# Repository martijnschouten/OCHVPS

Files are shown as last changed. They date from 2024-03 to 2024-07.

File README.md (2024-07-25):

# OCHVPS: Octo-Channel High Voltage Power Supply

This git contains all the files to produce your own octo channel high voltage power supply. This is a 2 kV, 8 channel, 10 W power supply. It has 8 half-bridge outputs, each switching at up to 1 kHz. It can be used as 4 full bridges. Current monitoring on each channel. Designed to drive capacitive loads

HVPS

A block diagram of the power suply can be found below
HVPS_block

The source code of the Python GUI can be found in this [github repository](https://github.com/martijnschouten/OCHVPS_SW)

The source code of firmware running on microcontroller inside the board can be found in this [github repository](https://github.com/martijnschouten/OCHVPS_FW)

Some more information can be found in the [user's manual](https://github.com/martijnschouten/OCHVPS/blob/v1.0/1_DOC/OCHVPS_V1.0_User_Manual.pdf).

If your just interested in the schematic, that can be found [here](https://github.com/martijnschouten/OCHVPS/blob/v1.0/2_HW/PDF/ochvps_v1.0.pdf) 

OCHVPS © 2021-2024 by MBE <ochvps@proton.me>

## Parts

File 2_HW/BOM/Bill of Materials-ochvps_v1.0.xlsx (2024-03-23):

Designator | Quantity | Supplier 1 | Supplier Part Number 1 | Name | Description
C1, C3 | 2 | Farnell | 9227865 | C1206C105K3RACTU | Chip Capacitor, 1 uF, +/- 10%, 25 V, -55 to 125 degC, 1206 (3216 Metric), RoHS, Tape and Reel
C2, C4, C28 | 3 | Mouser | 80-C0603C104K3R | C0603C104K3RACTU | CAP CER 0.1UF 25V X7R 0603
C5, C6, C7, C8, C9, C10, C11, C12, C13, C14, C16, C17, C19, C20, C21, C22, C60_HB1, C60_HB2, C60_HB3, C60_HB4, C60_HB5, C60_HB6, C60_HB7, C60_HB8, C61_HB1, C61_HB2, C61_HB3, C61_HB4, C61_HB5, C61_HB6, C61_HB7, C61_HB8 | 32 | Mouser | 581-06033C104KAT4A | 06033C104KAT4A | CAP CER 0.1UF 25V X7R 0603
C15 | 1 | Digi-Key | 399-7411-1-ND | C0805C106K8RACTU | 0805 C 10uF Ceramic Multilayer Capacitor; 10 V; +125degC; X7R Dielectric; +/-10%
C18 | 1 | DigiKey | 445-5964-1-ND | C1608X5R1E225K080AB | Multilayer Ceramic Capacitors 2.2μF ±10% 25V X5R SMD 0603
C23, C24 | 2 | Digi-Key | 478-1167-1-ND | 06035A220JAT2A | Cap Ceramic 22pF 50V C0G 5% SMD 0603 125C Paper T/R
C25 | 1 | Digikey | P15460CT-ND | EEH-ZC1E560P | Cap Aluminum Polymer Hybrid 56uF 25VDC 20% (6.3 X 5.8mm) SMD 0.05 Ohm 900mA 4000h 125C Embossed T/R
C26 | 1 | Farnell | 3605828 | 16SVPG330MX | Capacitor, Polymer Aluminum, Radial, 7mOhm, 330 CAP, 16V, SVPG, Surface Mount
C27, C30, C55, C58, C62_HB1, C62_HB2, C62_HB3, C62_HB4, C62_HB5, C62_HB6, C62_HB7, C62_HB8, C63_HB1, C63_HB2, C63_HB3, C63_HB4, C63_HB5, C63_HB6, C63_HB7, C63_HB8 | 20 | Digikey | 445-1316-1-ND | C1608X7R1E104K080AA | TDK - C1608X7R1E104K080AA - Keramikvielschichtkondensator, SMD, 0.1 µF, 25 V, 0603 [Metrisch 1608], ± 10%, X7R, C Series
C29, C31 | 2 | Digikey | 399-C0805C226M8PAC7210CT-ND | C0805C226M8PAC7210 | Cap, 22UF, 10V, Mlcc, 0805;
C32, C48 | 2 | Digikey | 478-6637-1-ND | TCJD476M025R0060 | CAP TANT POLY 47UF 25V 2917
C33, C34, C35 | 3 | Digikey | 445-5720-1-ND | CGA6P1X7R1E106M250AC | Multilayer Ceramic Capacitors MLCC - SMD/SMT 1210 10uF 25volts X7R 20% T=2.5mm
C36, C37, C42 | 3 | Mouser | 581-06033D105MAT2A | 06033D105MAT2A | Cap Ceramic 1uF 25V X5R 20% SMD 0603 85C Paper T/R
C38, C49 | 2 | DigiKey | 445-7348-1-ND | C1005X7R1E104K050BB | TDK - C1005X7R1E104K050BB - SMD Multilayer Ceramic Capacitor, 0.1 µF, 25 V, 0402 [1005 Metric], ± 10%, X7R, C Series TDK
C39 | 1 | DigiKey | 445-6893-1-ND | CGA2B3X7R1H103K050BB | CAP CER 10000PF 50V X7R 0402
C40, C41 | 2 | DigiKey | 490-6049-1-ND | GCM188L81H104KA57D | MURATA - GCM188L81H104KA57D - CAP, MLCC, AEC-Q200, X8L, 0.1UF, 0603
C43, C44, C45, C46 | 4 | Mouser | 810-CGA5L1X7R1E106K | CGA5L1X7R1E106K160AC | CAP CERAMIC, 10UF, 25V, X7R, 1206; Product Range:TDK - CGA Series; Capacitance:10µF; Capacitance Tolerance:± 10%; Dielectric Characteristic:X7R; Voltage Rating:25V; Ceramic Capacitor Case:1206 ^3216 Metric]; Packaging:Cut Tape; MSL:-
C47 | 1 | Digikey | 399-16637-1-ND | T521D226M035ATE060 | Cap Tant Polymer 22uF 35V D CASE 20% (7.3 X 4.3 X 2.8mm) SMD 7343-31, D 60 mOhm 125°C T/R
C50 | 1 | Digi-Key | 445-5607-1-ND | CGA2B2X7R1H472K050BA | CAP CER 4700PF 50V X7R 0402
C51 | 1 | Digikey | 490-14349-1-ND | GCM1555C1H101FA16D | 0402 50V C0G 100pF 1% multilayer ceramic capacitor
C52 | 1 | DigiKey | 445-9118-1-ND | C1608X6S1C475K080AC | Cap Ceramic 4.7uF 16V X6S 10% SMD 0603 105C Paper T/R
C53 | 1 | Mouser | 581-08055C334KAT2A | 08055C334KAT2A | CAP CER 0.33UF 50V X7R 0805
C54, C59 | 2 | Digikey | 445-1287-1-ND | C1608C0G1H331J080AA | C Series 0603 330 pF 50 V ±5 % Tolerance C0G SMT Multilayer Ceramic Capacitor
C56, C57 | 2 | Mouser | 581-06035A100J | 06035A100JAT2A | AVX - 06035A100JAT2A - SMD Multilayer Ceramic Capacitor, 10 pF, 50 V, 0603 [1608 Metric], ± 5%, C0G / NP0, AVX 0603 MLCC
D1 | 1 | Digikey | F3157CT-ND | SP0504BAHTG | TVS DIODE 5.5V 8.5V SOT23-5
D2, D3, D4, D5 | 4 | Digikey | 641-1326-1-ND | CDBW0520L-G | DIODE SCHOTTKY 20V 500MA SOD123
D6 | 1 | Mouser | 863-SZMM3Z3V0T1G | SZMM3Z3V0T1G | Zener Diodes ZEN SOD323 REG 0.2W
FB1 | 1 | Digikey | 490-11045-1-ND | BLM21BD331SN1D | FERRITE BEAD 330 OHM 0805 1LN
H_GND | 1 | Digikey | 486-3654-ND | 0040.1101 | Test Jack; 2mm; 10A; PCB Mt; Single Cntct; 90-Degree; Thrmoplstc; Black; UL94V-2; PB 1101
H_HV1, H_HV2, H_HV3, H_HV4, H_HV5, H_HV6, H_HV7, H_HV8 | 8 | Digikey | 486-3655-ND | 0040.1102 | Test Jack; 2mm; 10A; PCB Mt; Single Cntct; 90-Degree; Thrmoplstc; Red; UL94V-2; PB 1101
J1 | 1 | Digikey | CP-063AH-ND | PJ-063AH | CONN PWR JACK 2X5.5MM SOLDER
J2 | 1 | Newark | 67T2260 | 10118194-0001LF | Micro USB B Type Receptacle, 1.8 A, -55 to 85 degC, 5-Pin SMD, RoHS, Tape and Reel
J3, J4 | 2 |  |  | CON10A
L1 | 1 | Mouser | 652-SRP1245A-4R7M | SRP1245A-4R7M | BOURNS SRP1245A-4R7M Surface Mount Power Inductor, SRP1245A Series, 4.7 H, 12 A, 27 A, Shielded, 0.015 ohm
LED1, LED3 | 2 | Digikey | 732-4983-1-ND | 150080GS75000 | SMD LED green 3.5 V 0805, 150080GS75000, Würth Elektronik
LED2 | 1 | Digikey | 350-2044-1-ND | 598-8170-107F | Single Color, 2 V, -30 to 85 degC, 2-Pin SMD (0805), RoHS, Tape and Reel
P1 | 1 | Digi-Key |  | FTSH-105-01-F-DV-K | Conn Unshrouded Header HDR 10 POS 1.27mm Solder ST SMD T/R
Q1 | 1 | Digikey | SSM3J358RLFCT-ND | SSM3J358R,LF | Small Low ON Resistance MOSFET P-Channel 20V 6A 3-Pin SOT-23F T/R
Q2, Q3 | 2 | Digikey | 296-49601-1-ND | CSD17579Q5A | MOSFET 30V N-Chan NexFET? Pwr MOSFET 8-VSONP
R1 | 1 | DigiKey | 311-47KGRCT-ND | RC0603JR-0747KL | Thick Film Resistor
R2, R3 | 2 | Farnell | 4013304 | RC0603FR-1333RL | RC Series 0603 33 Ohm ±1 % 0.1 W ±100 ppm/°C Surface Mount Thick Film Resistor
R4 | 1 |  |  | RES_0 | Thick Film Resistor
R5, R6, R7, R44, R45, R46, R47 | 7 | DigiKey | 311-0.0GRCT-ND | RC0603JR-070RL | RES SMD 0 OHM JUMPER 1/10W 0603
R8 | 1 | Digikey | 541-3993-1-ND | CRCW06034K70JNEA | RES Thick Film, 4.7kΩ, 5%, 0.1W, 200ppm/°C, 0603
R9, R10, R12, R13, R15, R16, R31, R41, R48_HB1, R48_HB2, R48_HB3, R48_HB4, R48_HB5, R48_HB6, R48_HB7, R48_HB8, R53_HB1, R53_HB2, R53_HB3, R53_HB4, R53_HB5, R53_HB6, R53_HB7, R53_HB8 | 24 | Digi-Key | 311-10.0KHRCT-ND | RC0603FR-0710KL | Res General Purpose Thick Film 0603 10K Ohm 1% 1/10W ±100ppm/°C Molded SMD Paper T/R
R11 | 1 | Mouser | 71-CRCW0603J-1.0M-E3 | CRCW06031M00JNEA | VISHAY - CRCW06031M00JNEA - SMD Chip Resistor, 0603 [1608 Metric], 1 Mohm, CRCW e3 Series, 75 V, Thick Film, 100 mW
R14, R17 | 2 | Digikey | 541-4022-1-ND | CRCW06032K20FKEA | SMD Resistor, Thick film 2.2 kOhm, ± 1 %, 0603, CRCW06032K20FKEA, Vishay
R18, R19 | 2 | Mouser | 71-CRCW060310K0FKEAC | CRCW060310K0FKEAC | Chip Resistor, 10 KOhm, +/- 1%, 100 mW, -55 to 155 degC, 0603 (1608 Metric), RoHS, Tape and Reel
R20, R40 | 2 | Digikey | 541-CRCW08054K70JNEBCT-ND | CRCW08054K70JNEB | VISHAY CRCW08054K70JNEB RES, THICK FILM, 4K7, 5%, 0.125W, 0805
R21 | 1 | Digikey | 541-CRCW08053K32FKEACCT-ND | CRCW08053K32FKEAC | Res Thick Film 0805 3.32K Ohm 1% 1/8W ±100ppm/°C Molded SMD Paper T/R
R22 | 1 | DigiKey | P1.07KHCT-ND | ERJ-3EKF1071V | Res Thick Film 0603 1.07K Ohm 1% 0.1W(1/10W) ±100ppm/C Pad SMD Automotive T/R
R23 | 1 | Digikey | 541-CRCW0805680RJNEBCT-ND | CRCW0805680RJNEB | Thick Film Resistors - SMD 1/8watt 680ohms 5%
R24 | 1 |  |  |  | Thick Film Resistor
R25 | 1 | Digikey | P37.4KDCCT-ND | ERA-2AEB3742X | RES SMD 37.4KOHM 0.1% 1/16W 0402
R26, R30 | 2 | Mouser | 603-RT0402BRE0710KL | RT0402BRE0710KL | RES SMD 10K OHM 0.1% 1/16W 0402
R27, R28 | 2 | Digi-Key | 311-1.00HRCT-ND | RC0603FR-071RL | Res General Purpose Thick Film 0603 1 Ohm 1% 1/10W ±200ppm/°C Molded SMD Paper T/R
R29 | 1 | DigiKey | P30.1KDCCT-ND | ERA-2AEB3012X | PANASONIC - ERA2AEB3012X - RES, 30K1, 0.1%, THIN FILM
R32 | 1 | Digikey | 541-49.9KAVCT-ND | CRCW040249K9DHEDP | RES SMD 49.9KOHM 0.5% 1/16W 0402
R33 | 1 | DigiKey | RMCF0402ZT0R00CT-ND | RMCF0402ZT0R00 | RES 0 OHM JUMPER 1/16W 0402
R34 | 1 | DigiKey | P0.01BVCT-ND | ERJ-8CWFR010V | RES 0.01 OHM 1% 1W 1206
R35, R36, R58_HB1, R58_HB2, R58_HB3, R58_HB4, R58_HB5, R58_HB6, R58_HB7, R58_HB8, R59_HB1, R59_HB2, R59_HB3, R59_HB4, R59_HB5, R59_HB6, R59_HB7, R59_HB8, Rsh1 | 19 | Digikey | RNCF0603AKT10R0CT-ND | RNCF0603AKT10R0 | RES 10 OHM 0.05% 1/10W 0603
R37 | 1 | Digikey | 541-CRCW0402150KFKTDCT-ND | CRCW0402150KFKTD | RES SMD 150K OHM 1% 1/16W 0402
R38 | 1 | Digikey | YAG3260CT-ND | RC0402FR-0793K1L | Res Thick Film 0402 93.1K Ohm 1% 0.063W(1/16W) ±100ppm/C Molded SMD Paper T/R
R39 | 1 | Mouser | 71-CRCW0402-10K | CRCW040210K0FKTD | Res Thick Film 0402 10K Ohm 1% 0.063W(1/16W) }100ppm/ ? SMD Automotive Paper T/R
R42 | 1 | Digikey | SM102031006FE-ND | SM102031006FE | Thick Film Resistors - Through Hole 100M ohms 1%
R43 | 1 | Mouser | 660-RN73R1JTD1503B25 | RN73R1JTTD1503B25 | Res 150K Ohm 0.1% 1/10W 0603
R49_HB1, R49_HB2, R49_HB3, R49_HB4, R49_HB5, R49_HB6, R49_HB7, R49_HB8, R54_HB1, R54_HB2, R54_HB3, R54_HB4, R54_HB5, R54_HB6, R54_HB7, R54_HB8 | 16 | Mouser | 667-ERJ-14YJ101U | ERJ-14YJ101U | SISTOR, THICK FILM, 1210, 100 OHM, 5%, 500mW; Product Range:PANASONIC - ERJ Series; Resistance:100ohm; Power Rating:500mW; Resistance Tolerance:± 5%; Resistor Case Style:1210 ^3225 Metric]; Resistor Element Type:Thick Film; MSL:-
R50_HB1, R50_HB2, R50_HB3, R50_HB4, R50_HB5, R50_HB6, R50_HB7, R50_HB8, R55_HB1, R55_HB2, R55_HB3, R55_HB4, R55_HB5, R55_HB6, R55_HB7, R55_HB8 | 16 | Digikey | A140839CT-ND | RQ73C2B976KBTD | RQ732B 1206 976KΩ 0.4W 10ppm/°C 0.1% 200V
R51_HB1, R51_HB2, R51_HB3, R51_HB4, R51_HB5, R51_HB6, R51_HB7, R51_HB8, R56_HB1, R56_HB2, R56_HB3, R56_HB4, R56_HB5, R56_HB6, R56_HB7, R56_HB8 | 16 | Digikey | A139596CT-ND | RQ73C2B182KBTD | Thick Film Resistor
R52_HB1, R52_HB2, R52_HB3, R52_HB4, R52_HB5, R52_HB6, R52_HB7, R52_HB8, R57_HB1, R57_HB2, R57_HB3, R57_HB4, R57_HB5, R57_HB6, R57_HB7, R57_HB8 | 16 | Digikey | 764-1313-1-ND | PTN1206E7773BST1 | RES SMD 777K OHM 0.1% 0.4W 1206
Rsh2_HB1, Rsh2_HB2, Rsh2_HB3, Rsh2_HB4, Rsh2_HB5, Rsh2_HB6, Rsh2_HB7, Rsh2_HB8 | 8 | Digikey | 1712-CPF0805B3R01E1CT-ND | CPF0805B3R01E1 | Res Thin Film 3.01Ohm 0.1% 100mW 25ppm/°C 2-Pin 0805 SMD T/R
SW1 | 1 | Digikey | 401-2016-1-ND | PCM12SMTR | C & K COMPONENTS - PCM12SMTR - SWITCH, SPDT, 0.3A, 6VDC, SMD
SW2 | 1 | Digikey | CKN1779CT-ND | ES01MSABE | Slide Switch, ES Series, SPDT, Horizontal, SMD, 100 mA, 20 V ;RoHS Compliant: Yes
T1 | 1 | Digikey | 1297-1104-1-ND | 750313626 | WURTH ELEKTRONIK - 750313626 - TRANSFORMER, AEC-Q200, 1:2, 340UH, SMT
T2_HB1, T2_HB2, T2_HB3, T2_HB4, T2_HB5, T2_HB6, T2_HB7, T2_HB8, T3_HB1, T3_HB2, T3_HB3, T3_HB4, T3_HB5, T3_HB6, T3_HB7, T3_HB8 | 16 | Mouser | 747-IXTT02N450HV | IXTT02N450HV | Mosfet N-CH 4500V 0.2A TO268
U1 | 1 | Mouser | 634-CP2102-GM | CP2102-GM | Single-Chip USB to UART Bridge, 1024 Bytes EEPROM, -40 to 85 degC, 28-pin QFN, Tube
U2 | 1 | Digi-Key | MK60DN256VLQ10-ND | MK60DN256VLQ10 | ARM Microcontrollers - MCU KINETIS 256K
U3 | 1 | Digikey | 24AA08T-I/OTCT-ND | 24AA08T-I/OT | EEPROM, 256X8, Serial, CMOS, PDSO5
U4 | 1 | Digi-Key | LMZ22003TZ/NOPB-ND | LMZ22003TZ/NOPB | DC DC CONVERTER 0.8-6V 3A
U5 | 1 | Digikey | MAX253ESA+-ND | MAX253ESA+ | Transformer Dvr for Iso. RS-485/RS-232 I'face; Single Supply 5.0 or 3.3 V, SOIC8
U6 | 1 | Mouser | 595-TPS76550D | TPS76550D | IC REG LINEAR 5V 150MA 8SOIC
U7 | 1 | Mouser | 595-TPS55288RPMR | TPS55288RPMR | Switching Regulator, Average Current, 6.35A, 2400kHz Switching Freq-Max, PBCC26
U8 | 1 | Digikey | 1470-3292-ND | FS20-12 | DC-DC Converter; Through Hole; DIP; 10W; 2000V@5mA; 0.7-12V In; FS Series
U9 | 1 | Mouser | 595-AMC1302QDWVRQ1 | AMC1302QDWVRQ1 | Automotive ±50mV-Input High-Precision Reinforced Isolated Amplifier for Current Sensing 8-SOIC -40 to 125
U10_HB1, U10_HB2, U10_HB3, U10_HB4, U10_HB5, U10_HB6, U10_HB7, U10_HB8, U12_HB1, U12_HB2, U12_HB3, U12_HB4, U12_HB5, U12_HB6, U12_HB7, U12_HB8 | 16 | Digikey | LTC6994IDCB-1#TRMPBFCT-ND | LTC6994IDCB-1#TRMPBF | IC DELAY LINE 6-DFN
U11_HB1, U11_HB2, U11_HB3, U11_HB4, U11_HB5, U11_HB6, U11_HB7, U11_HB8, U13_HB1, U13_HB2, U13_HB3, U13_HB4, U13_HB5, U13_HB6, U13_HB7, U13_HB8 | 16 | Mouser | 769-APV1122A | APV1122A | Photovoltaic MOSFET driver, 5kV isolation, 6-DIP SMD, 8.7V/14uA output
U14_HB1, U14_HB2, U14_HB3, U14_HB4, U14_HB5, U14_HB6, U14_HB7, U14_HB8 | 8 | Digikey | 296-INA180B4QDBVRQ1CT-ND | INA180B4QDBVRQ1 | Low and High-Side Voltage Output Current-Sense Amplifier 1 Channel 200V/V 5-Pin SOT-23 T/R
Y1 | 1 | Mouser | 449-LFXTAL055663REEL | LFXTAL055663REEL | Crystal 8MHz ±20ppm (Tol) ±30ppm (Stability) 18pF FUND 150Ohm 4-Pin CSMD T/R

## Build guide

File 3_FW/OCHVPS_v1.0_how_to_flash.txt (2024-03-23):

########################################################################################################################
# @project    OCHVPS_v1.0
# @file       OCHVPS_v1.0_how_to_flash.txt
# @brief      Author:             MBE
#             Software version:   v1.00
#             Created on:         20.03.2024
#             Last modifications: 20.03.2024
#
# OCHVPS © 2021-2024 by MBE <ochvps@proton.me>
#
# This program is free software: you can redistribute it and/or modify it under the terms of the GNU Lesser General
# Public License as published by the Free Software Foundation, either version 3 of the License, or (at your option)
# any later version.
#
# This library is distributed in the hope that it will be useful, but WITHOUT ANY WARRANTY; without even the implied
# warranty of MERCHANTABILITY or FITNESS FOR A PARTICULAR PURPOSE.  See the GNU Lesser General Public License for more
# details.
#
# You should have received a copy of the GNU General Public License along with this library.  If not, see:
# <http://www.gnu.org/licenses/>.
#
# NO HELP WILL BE GIVEN IF YOU MODIFY THIS CODE !!!
########################################################################################################################

Materials:
- OCHVPS_v1.0 board
- J-Link			(model used: 	J-Link base V11.0)
- MCUXpresso 			(version used: 	MCUXpresso IDE 11.9.0 2144)

------------------------------------------------------------------------------------------------------------------------
						How to flash 

01. Open MCUXpresso

02. File => New=> Create a new C/C++ project...

03. In SDK Wizard, under "SDK MCUs" and "Target", select "K6x" and "MK60DN256xxx10" and click on "Next"

04. Give a Project name, a project name suffix (not mandatory) and set the location for your project. Then, select: 
- "MK60DN256VLQ10" under "device Packages"
- "C++ Project" under "Project Type"
And click on "Finish

05. Click on the "GUI Flash Tool" icon

06. In the "File to program" edit text, select "JTAG"

07. In the "File to program" edit text, click on File System and choose the "OCHVPS_v1.0.axf file

08. Click on "Run..." button

09. Click on "OK"

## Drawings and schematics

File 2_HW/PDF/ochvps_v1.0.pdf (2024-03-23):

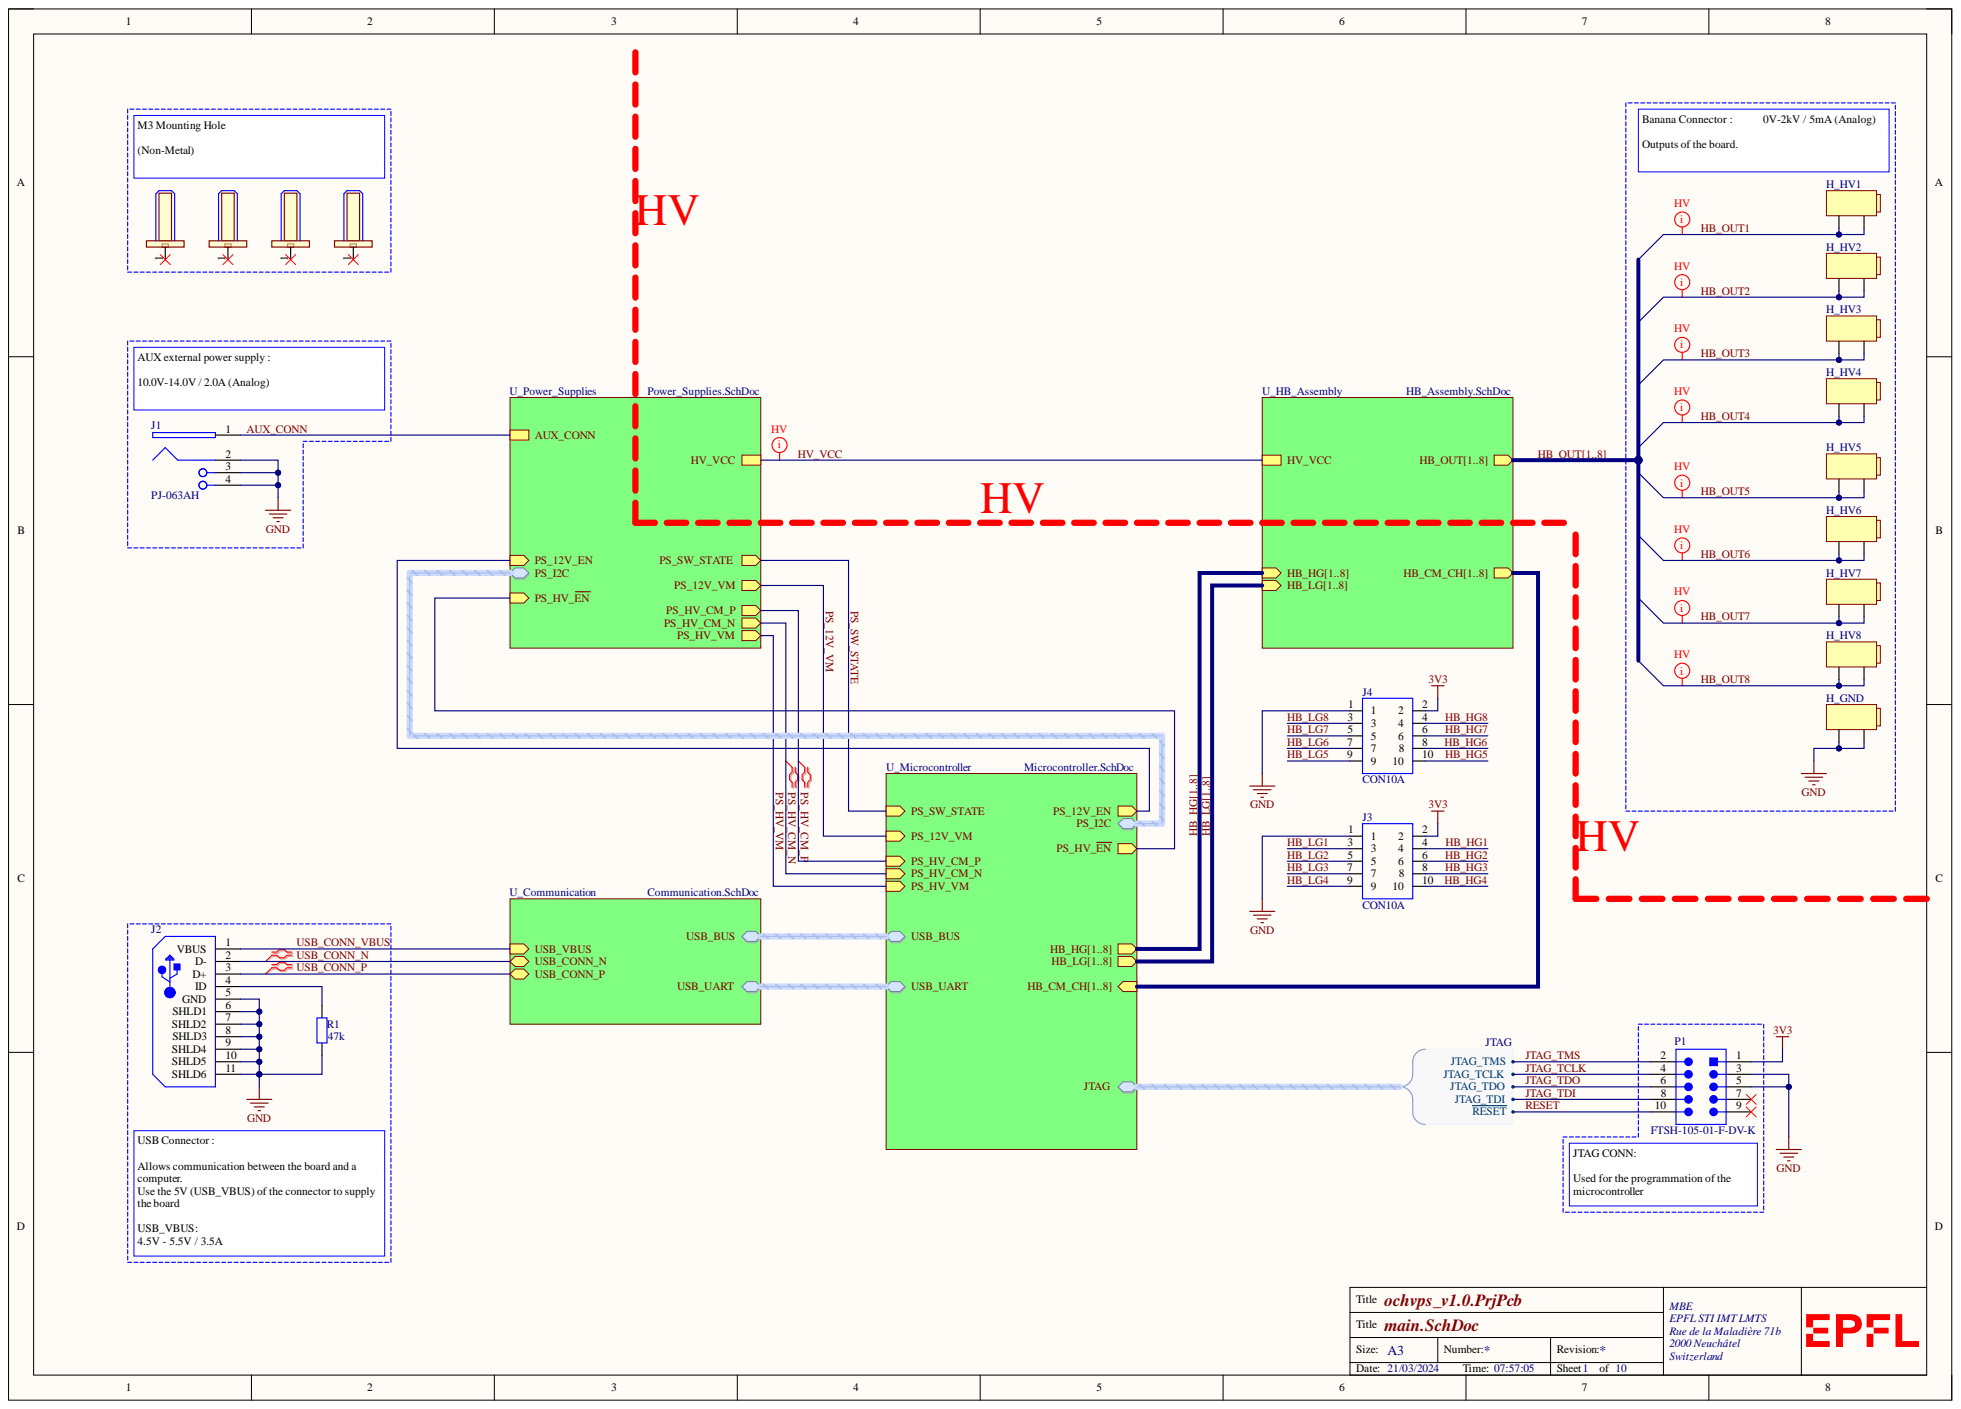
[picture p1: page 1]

10 1 SHLD5

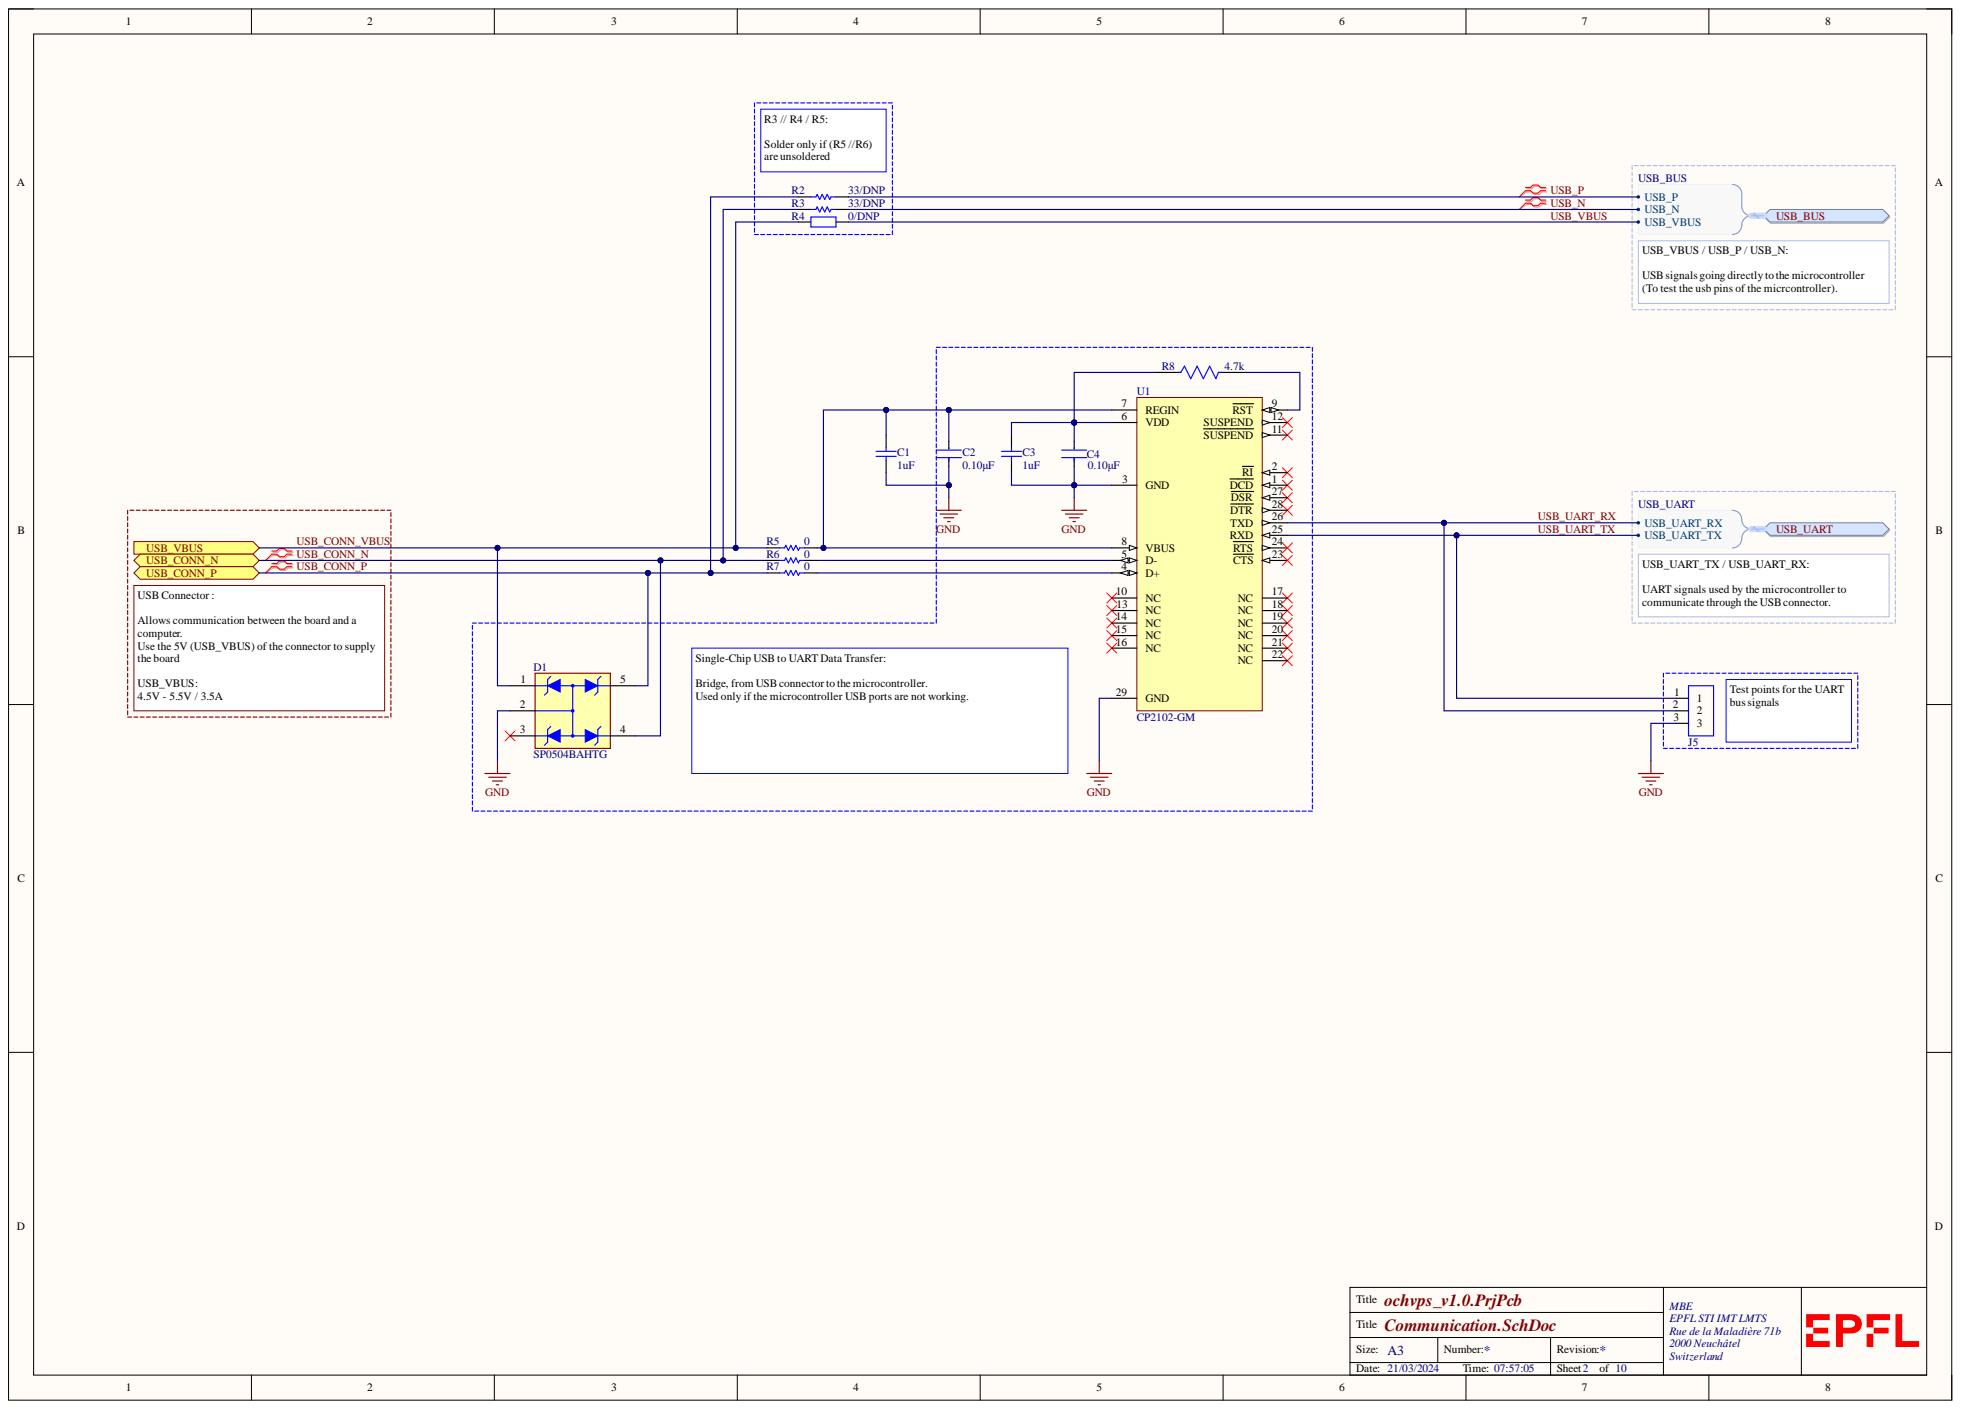
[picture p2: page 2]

USBsignals going directly to the microcontroller
(To test the usb pins of the micrcontroller).

C1 | C2 | | VDD 6 REGIN 7

GND 3

USB_UART_TX / USB_UART_RX: UART signals used by the microcontroller to communicate through the USBconnector.

Allows communication between the board and a
computer.
Use the 5V (USB_VBUS) of the connector to supply
the board

Single-Chip USB to UART Data Transfer:

Bridge, from USBconnectorto the microcontroller.
Used only if the microcontroller USB ports are not working.

Test points for the UART
bussignals

MBE
EPFL STI IMT LMTS
Rue de la Maladière 71b
2000 Neuchâtel
Switzerland

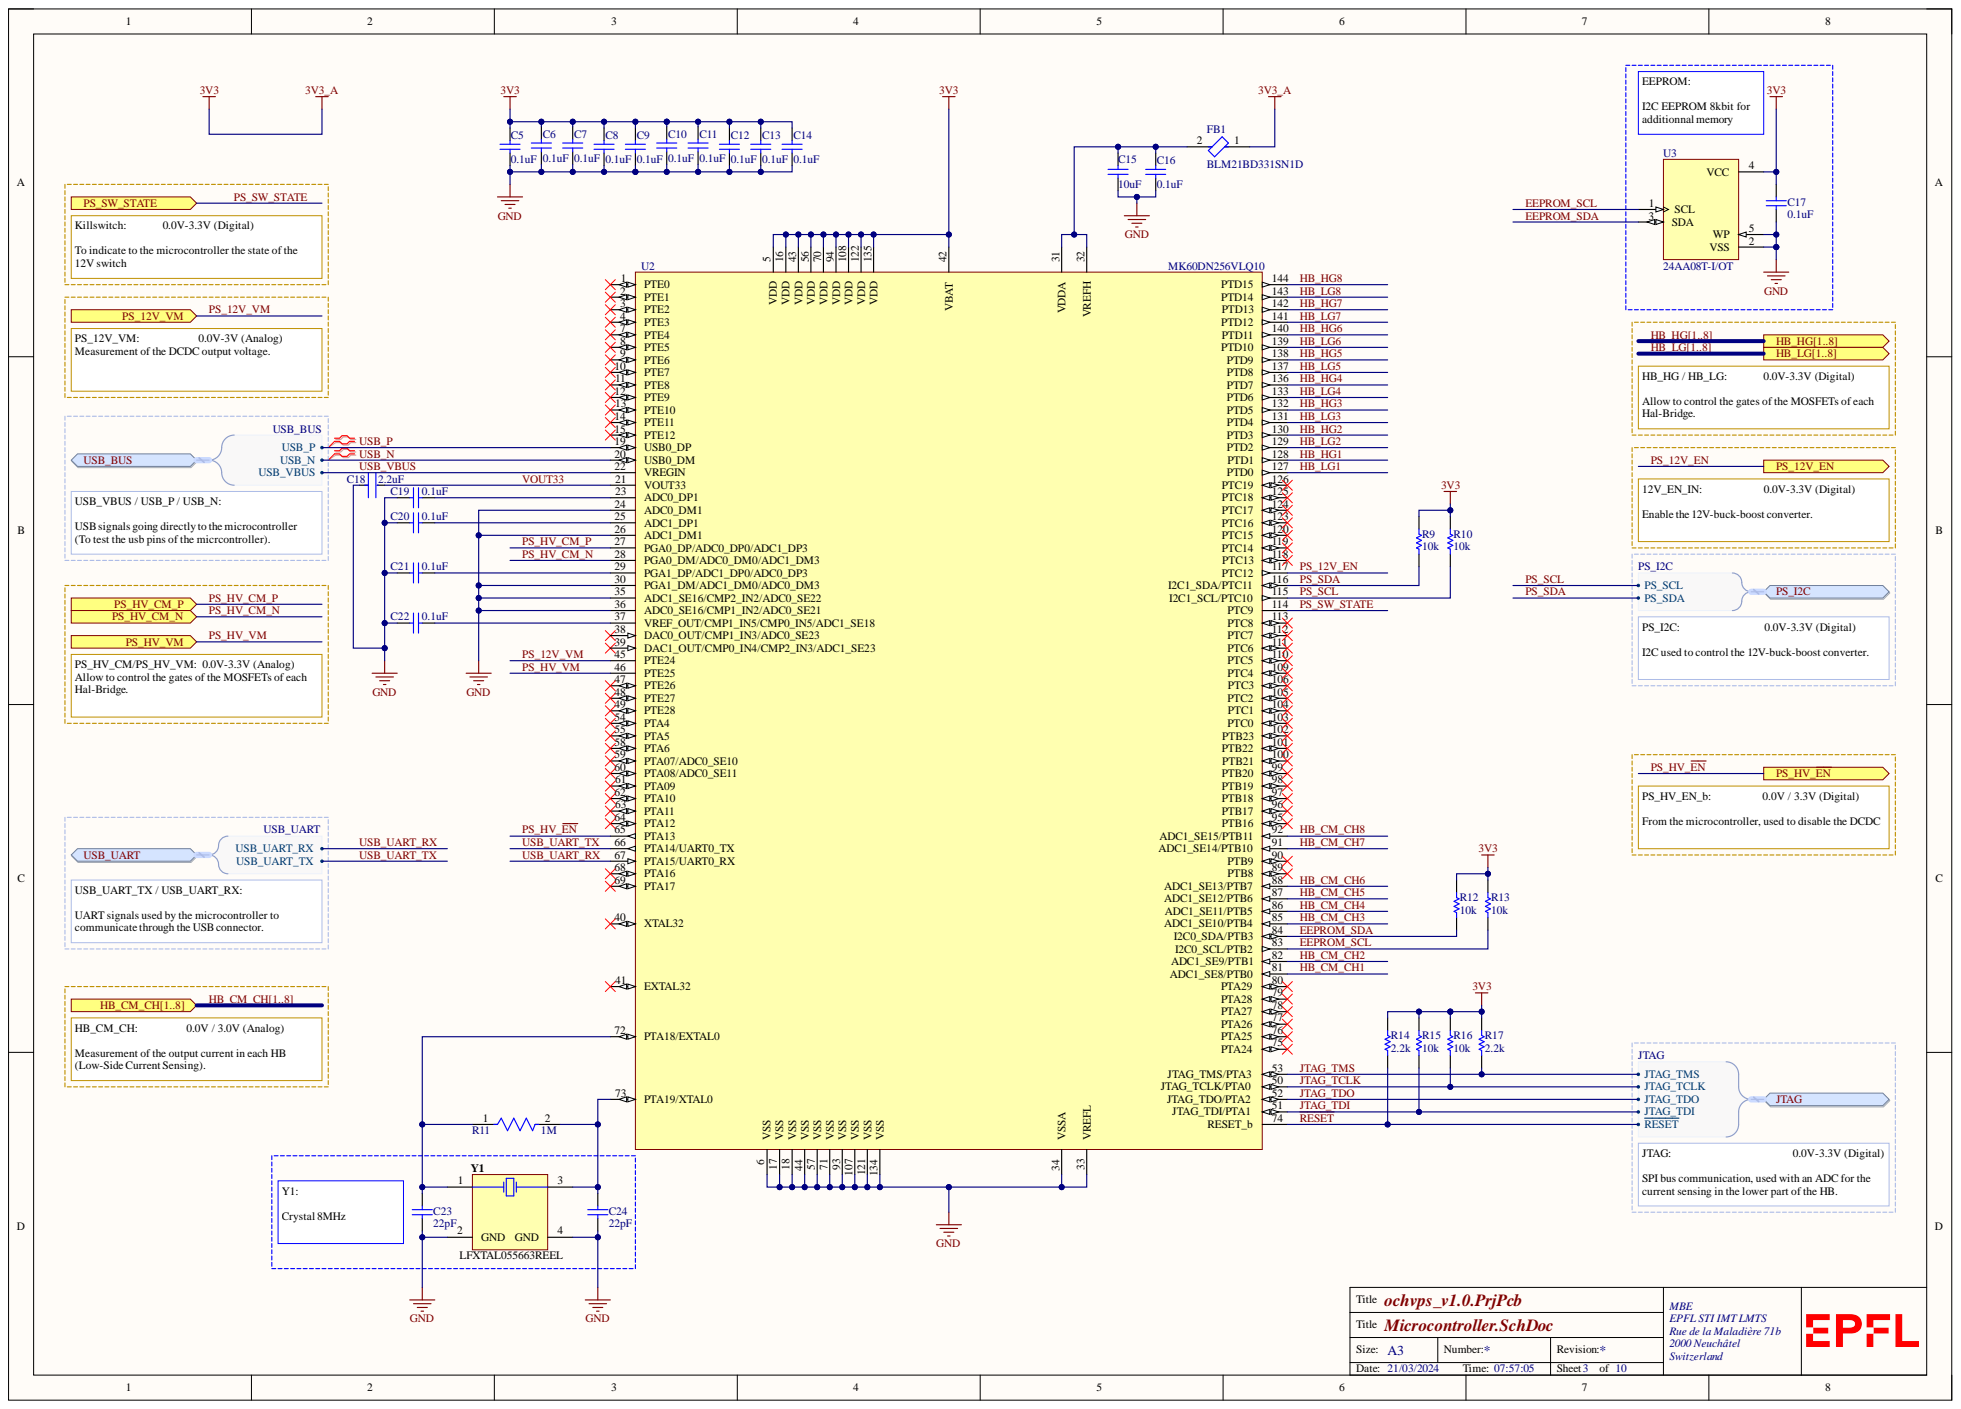
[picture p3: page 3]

the usb pins of

J TA G_T C L K
J TA G_T D O
J TA G_T D I

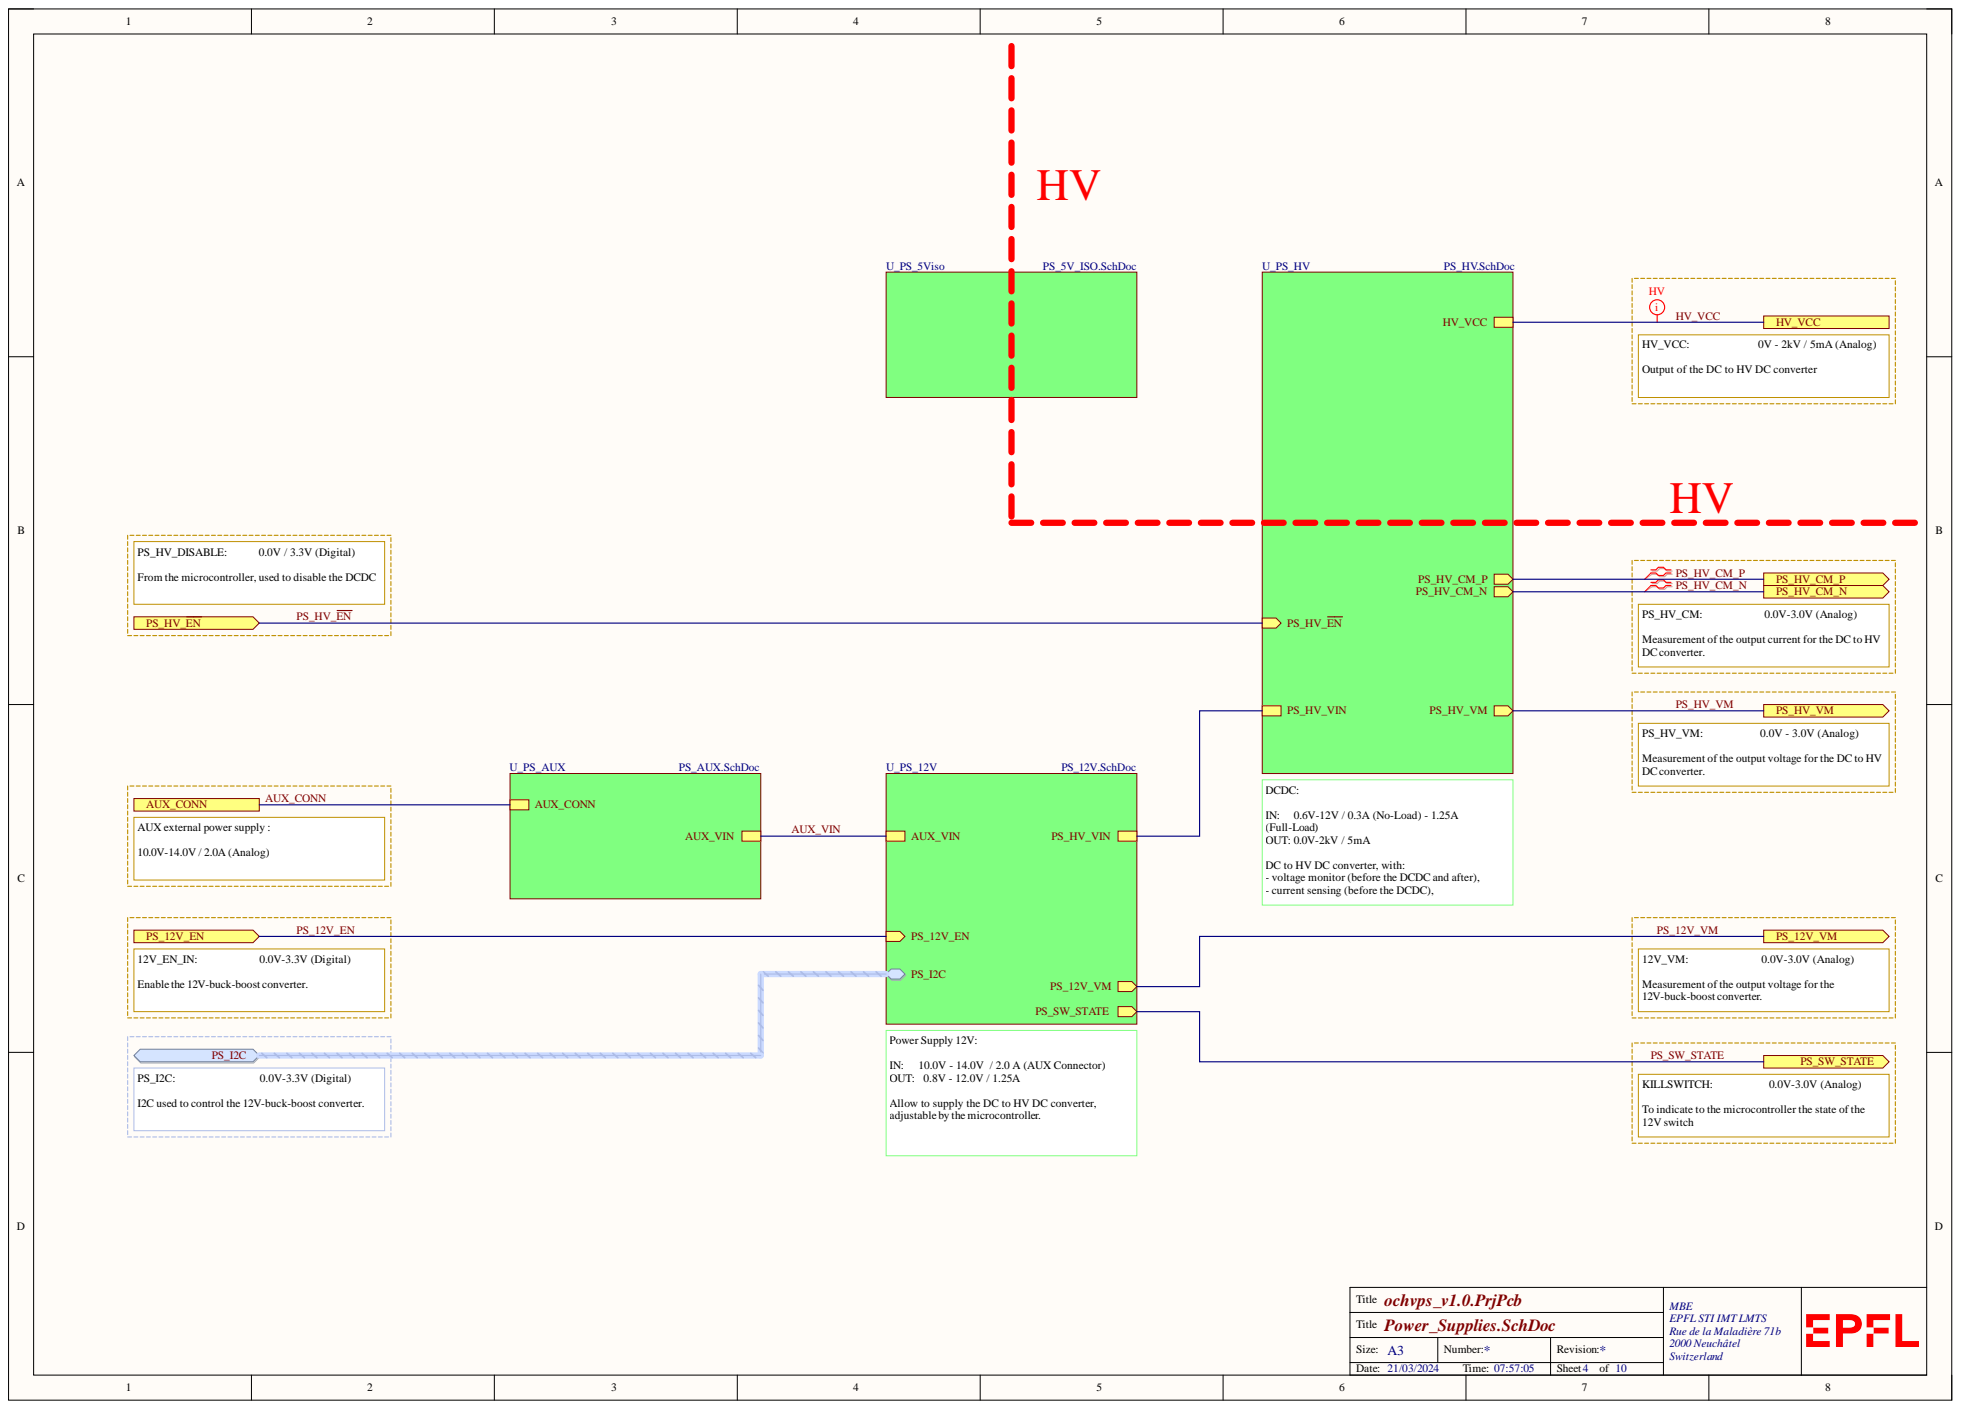
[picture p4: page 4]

Output of the DC to HV DC converter

From the microcontroller, used to disable the DCDC

Measurement of the output current for the DC to HV
DCconverter.

Measurement of the output voltage for the DC to HV

AUX external power supply :

DC to HV DC converter, with:
- voltage monitor (before the DCDC and after),
- current sensing (before the DCDC),

Enable the 12V-buck-boost converter.

Measurement of the output voltage for the
12V-buck-boost converter.

I2C used to control the 12V-buck-boost converter.

Allow to supply the DC to HV DC converter,
adjustable by the microcontroller.

To indicate to the microcontroller the state of the
12V switch

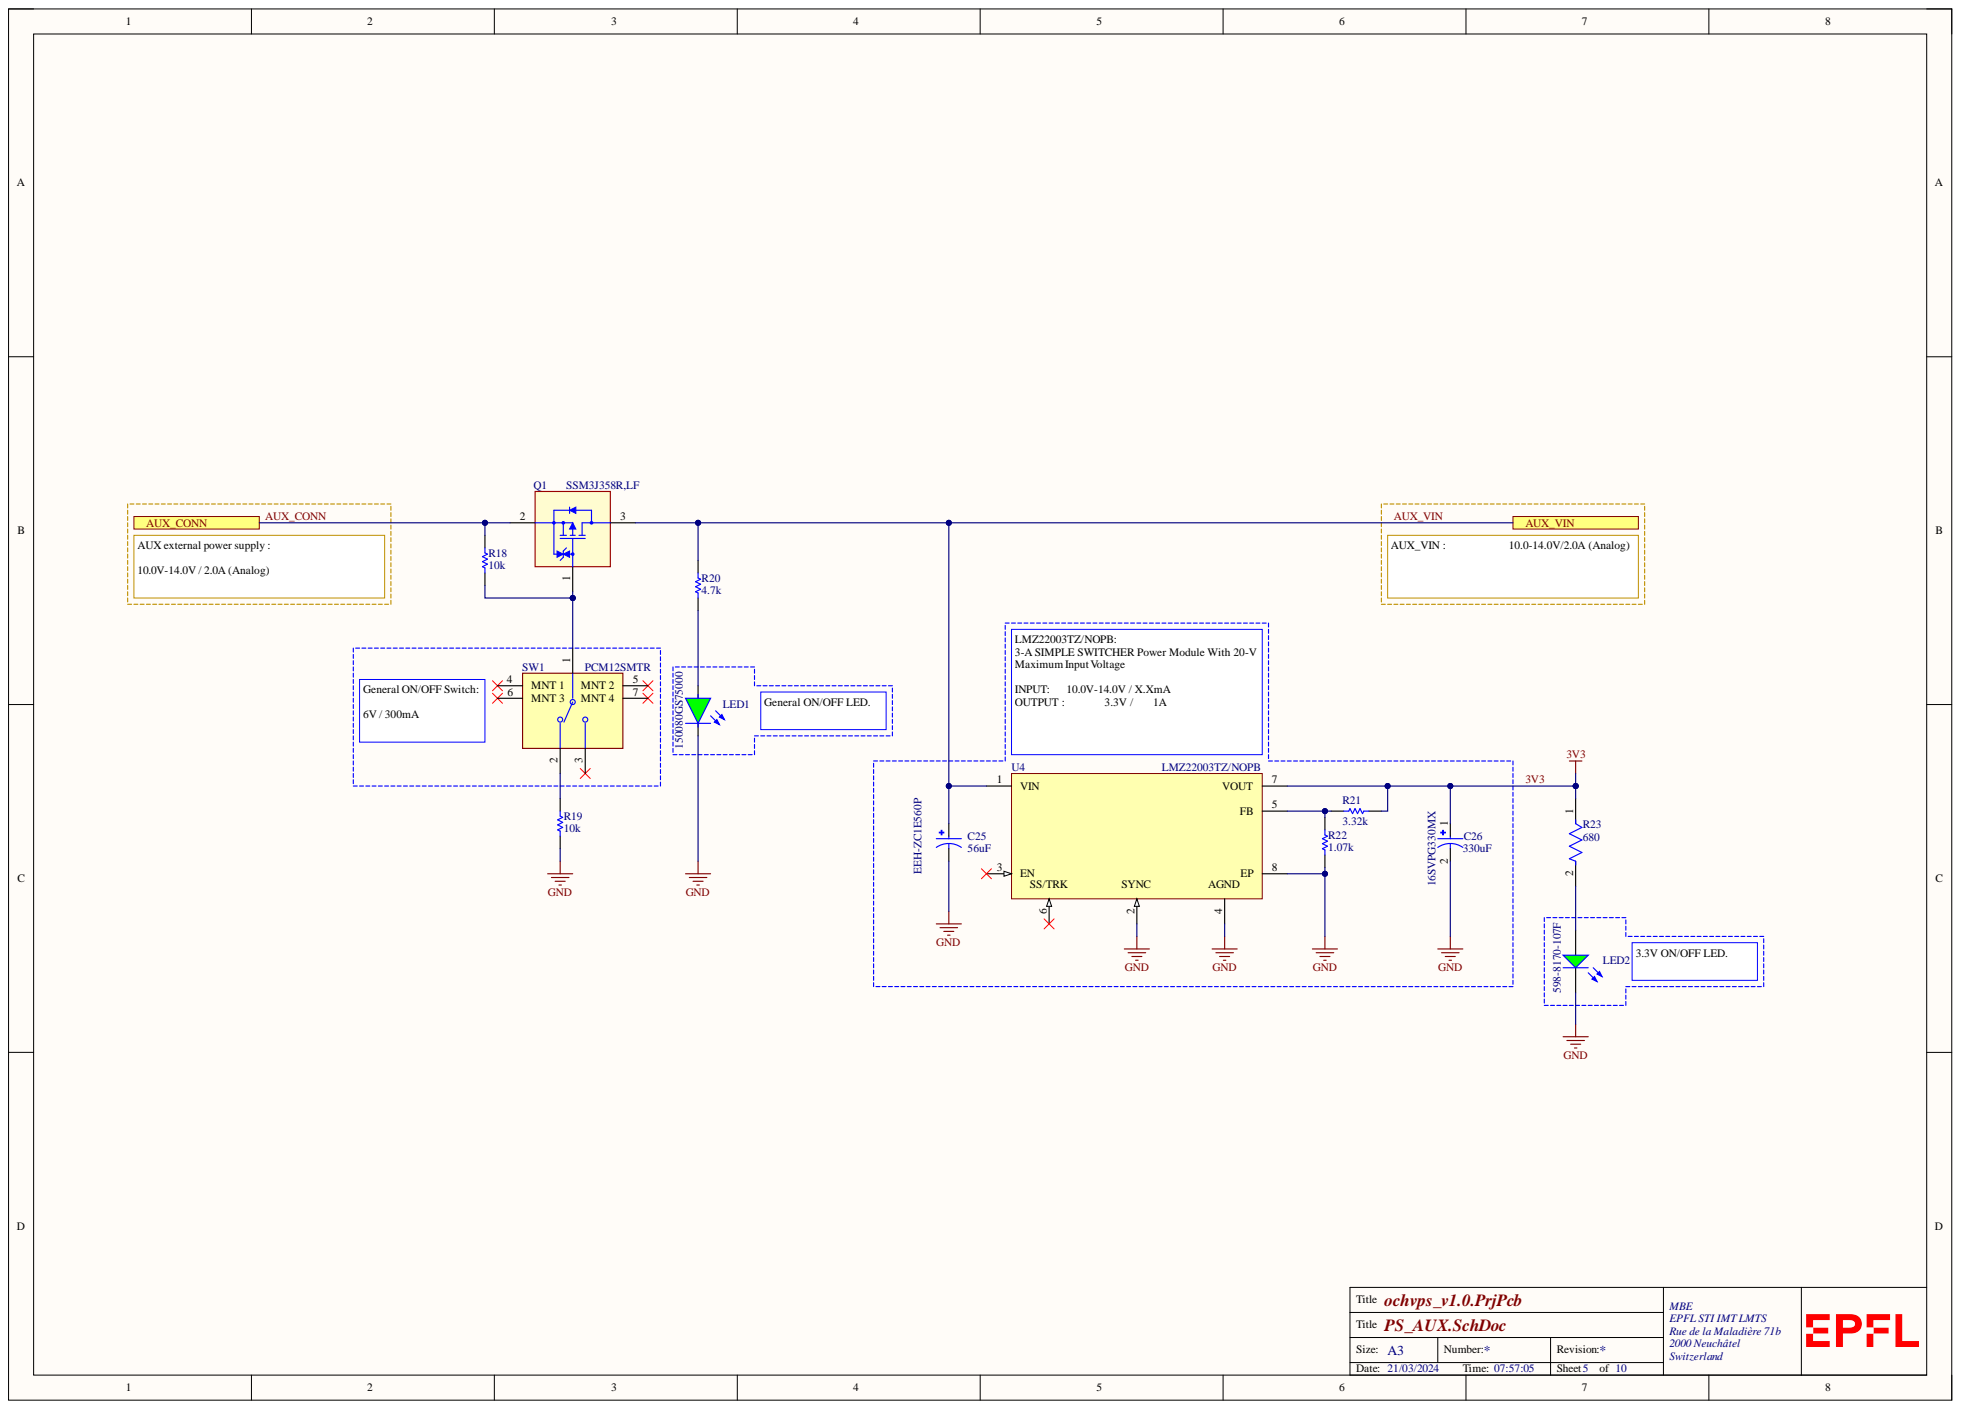
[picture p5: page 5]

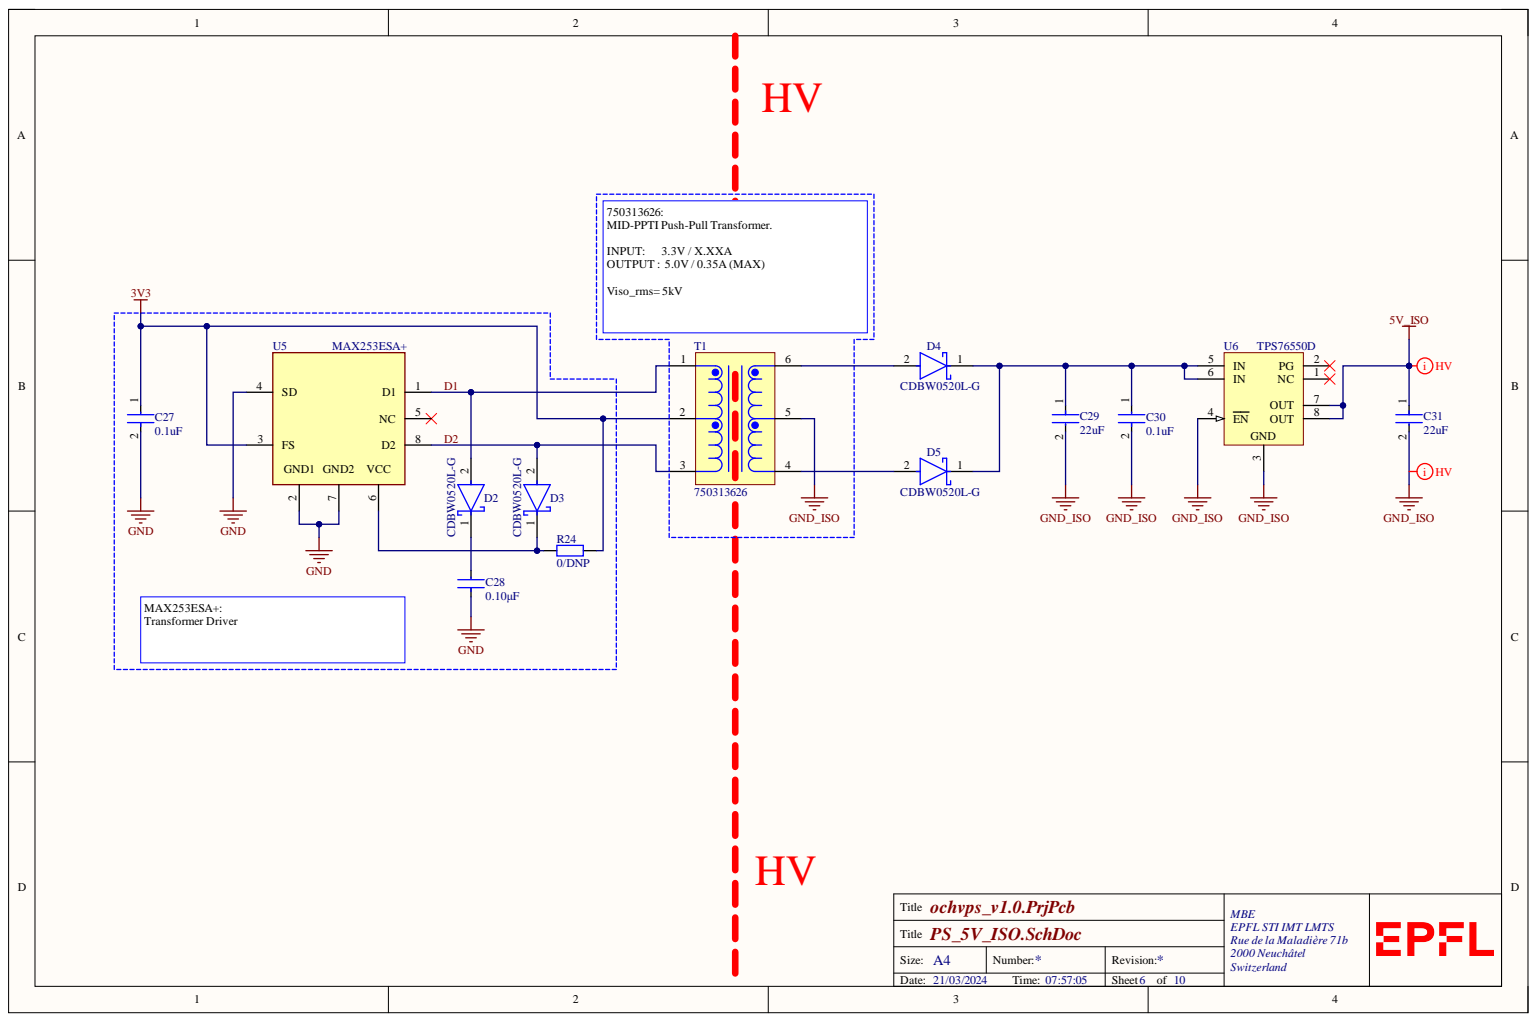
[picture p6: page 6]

Size : A 4 | N umb er : * | Rev i s i o n : *
Dat e : / / T ime : : : | | Shee t o f

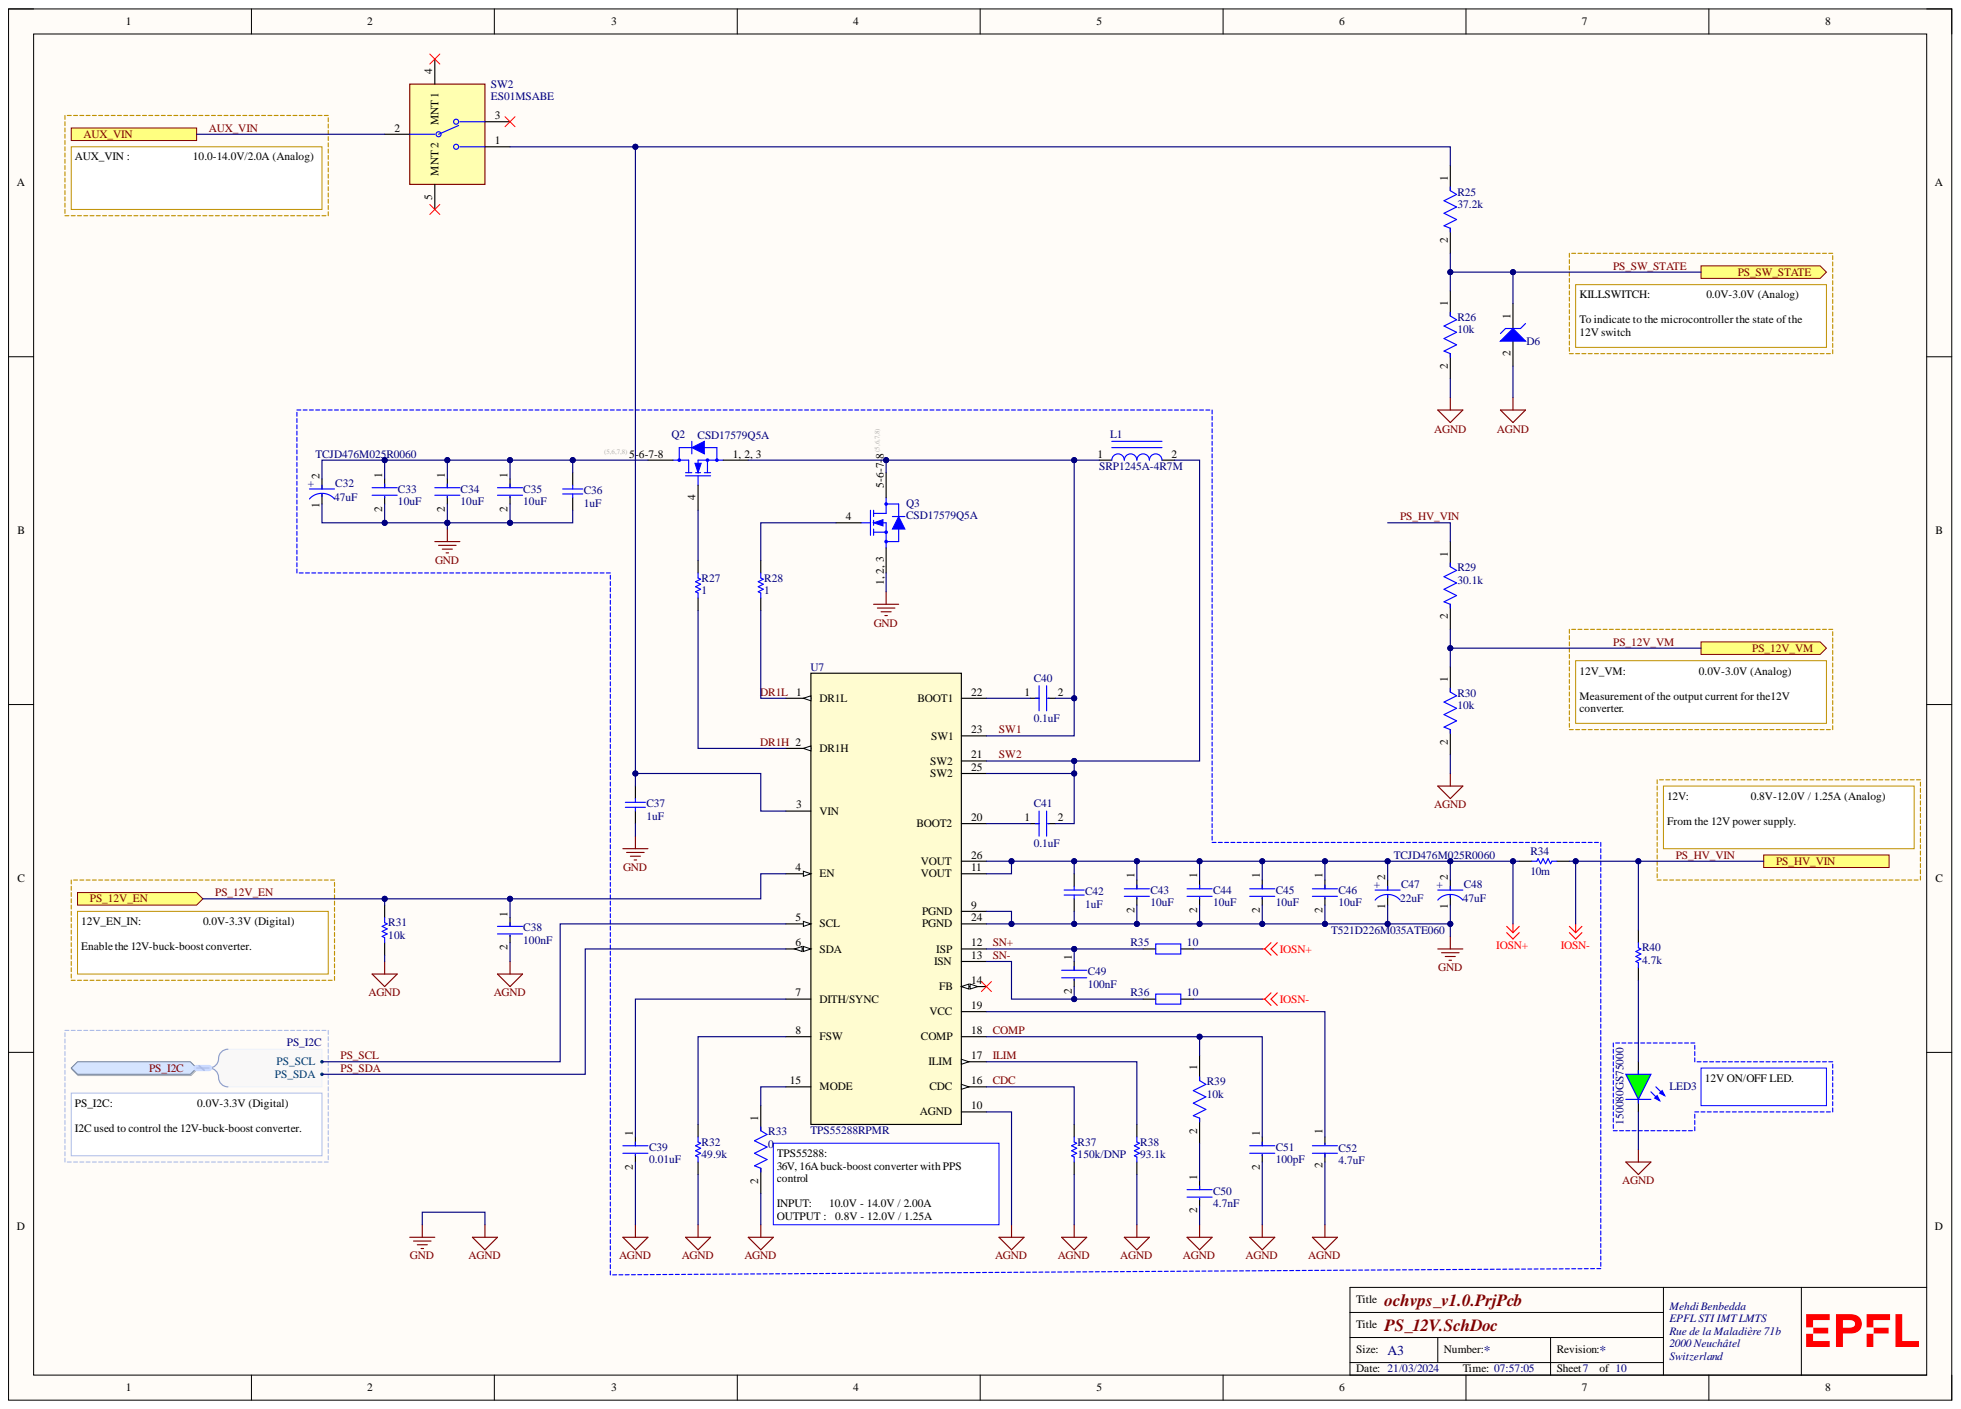
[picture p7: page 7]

To indicate to the microcontroller the state of the
12V switch

Measurement of the output current for the12V
converter.

From the 12V power supply.

C38 10k | | SDA 6

Enable the 12V-buck-boost converter.

AGND | AGND | | DITH/SYNC 7 | SN-

COMP

ILIM | R39

I2C used to control the 12V-buck-boost converter.

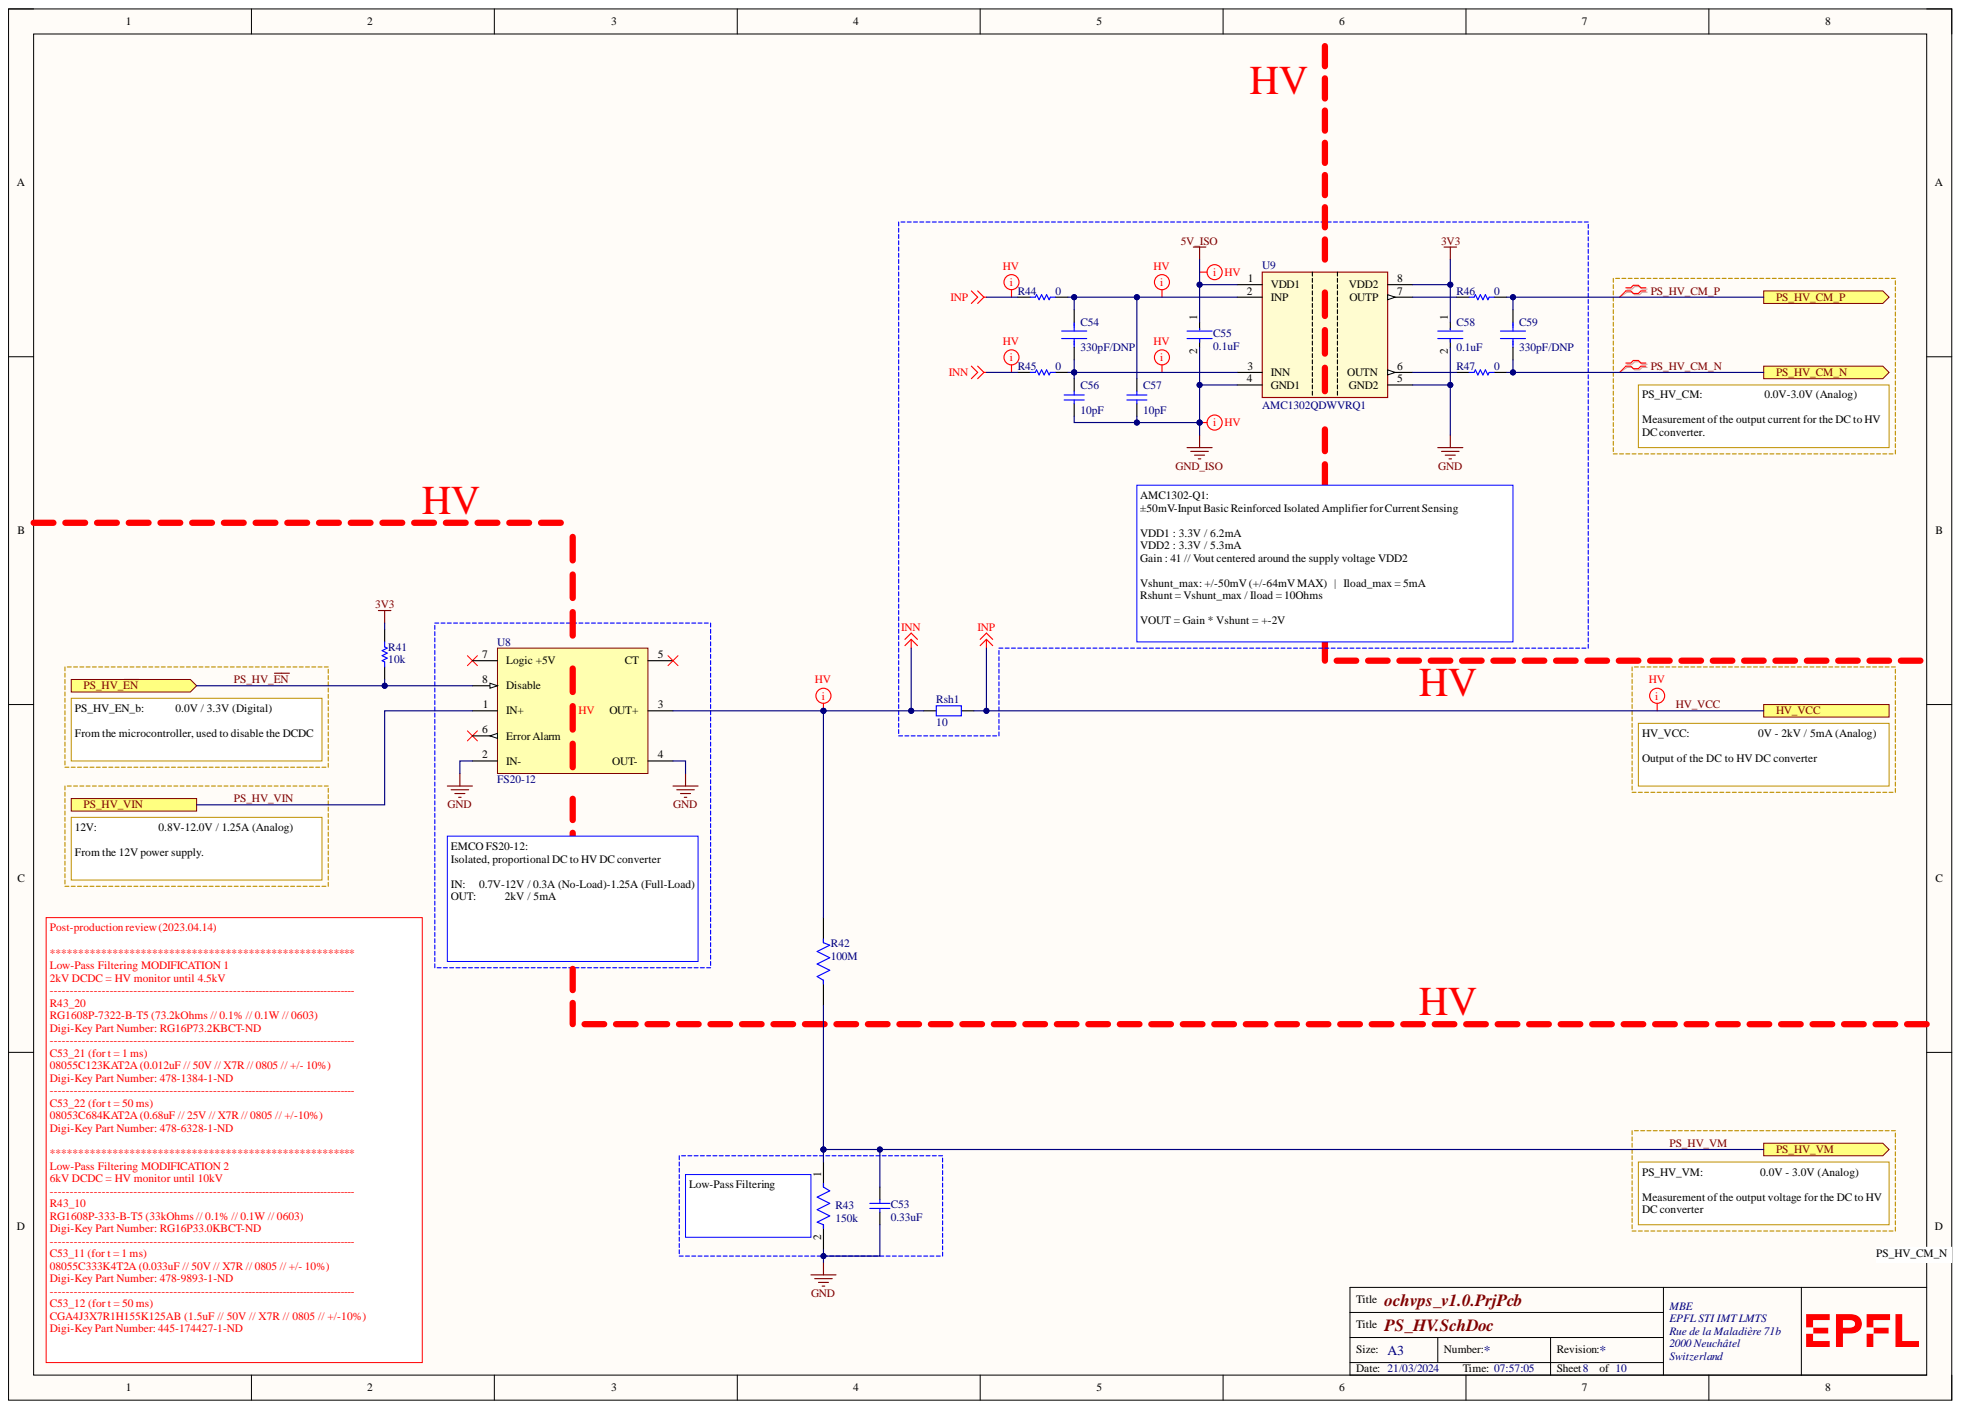
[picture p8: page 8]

Measurement of the output current for the DC to HV
DCconverter.

AMC1302-Q1:
±50mV-InputBasic Reinforced Isolated AmplifierforCurrent Sensing

VDD1 : 3.3V / 6.2mA
VDD2 : 3.3V / 5.3mA
Gain : 41 // Vout centered around the supply voltage VDD2

From the microcontroller, used to disable the DCDC

Output of the DC to HV DC converter

EMCO FS20-12:
Isolated, proportional DC to HV DC converter

From the 12V power supply.

Measurement of the output voltage for the DC to HV
DC converter

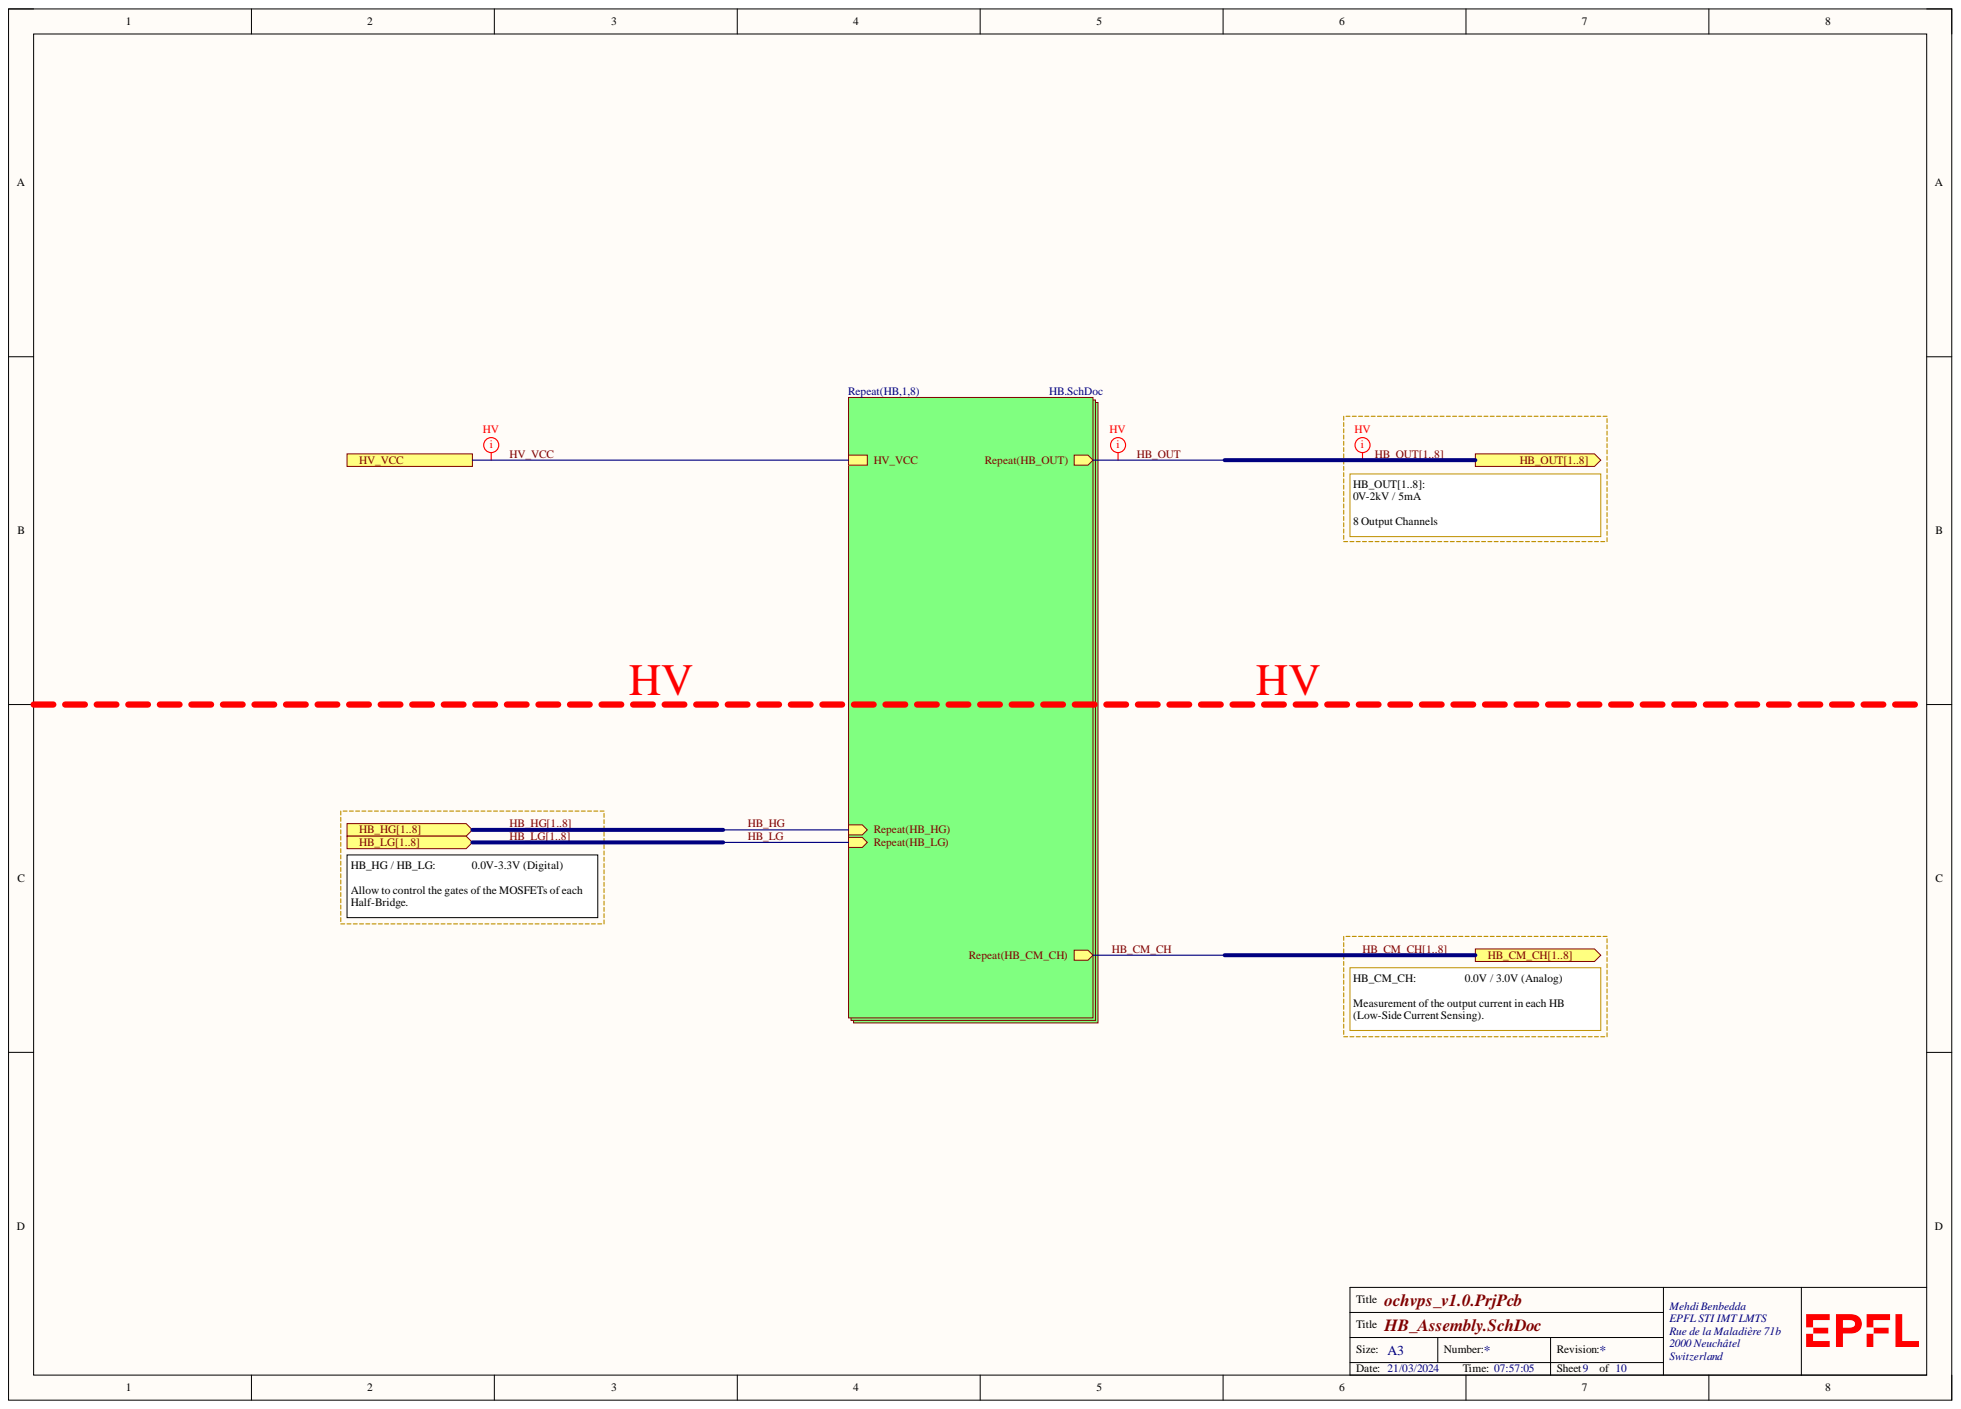
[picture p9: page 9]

Allow to control the gates of the MOSFETs of each
Half-Bridge.

Measurement of the output current in each HB
(Low-Side Current Sensing).

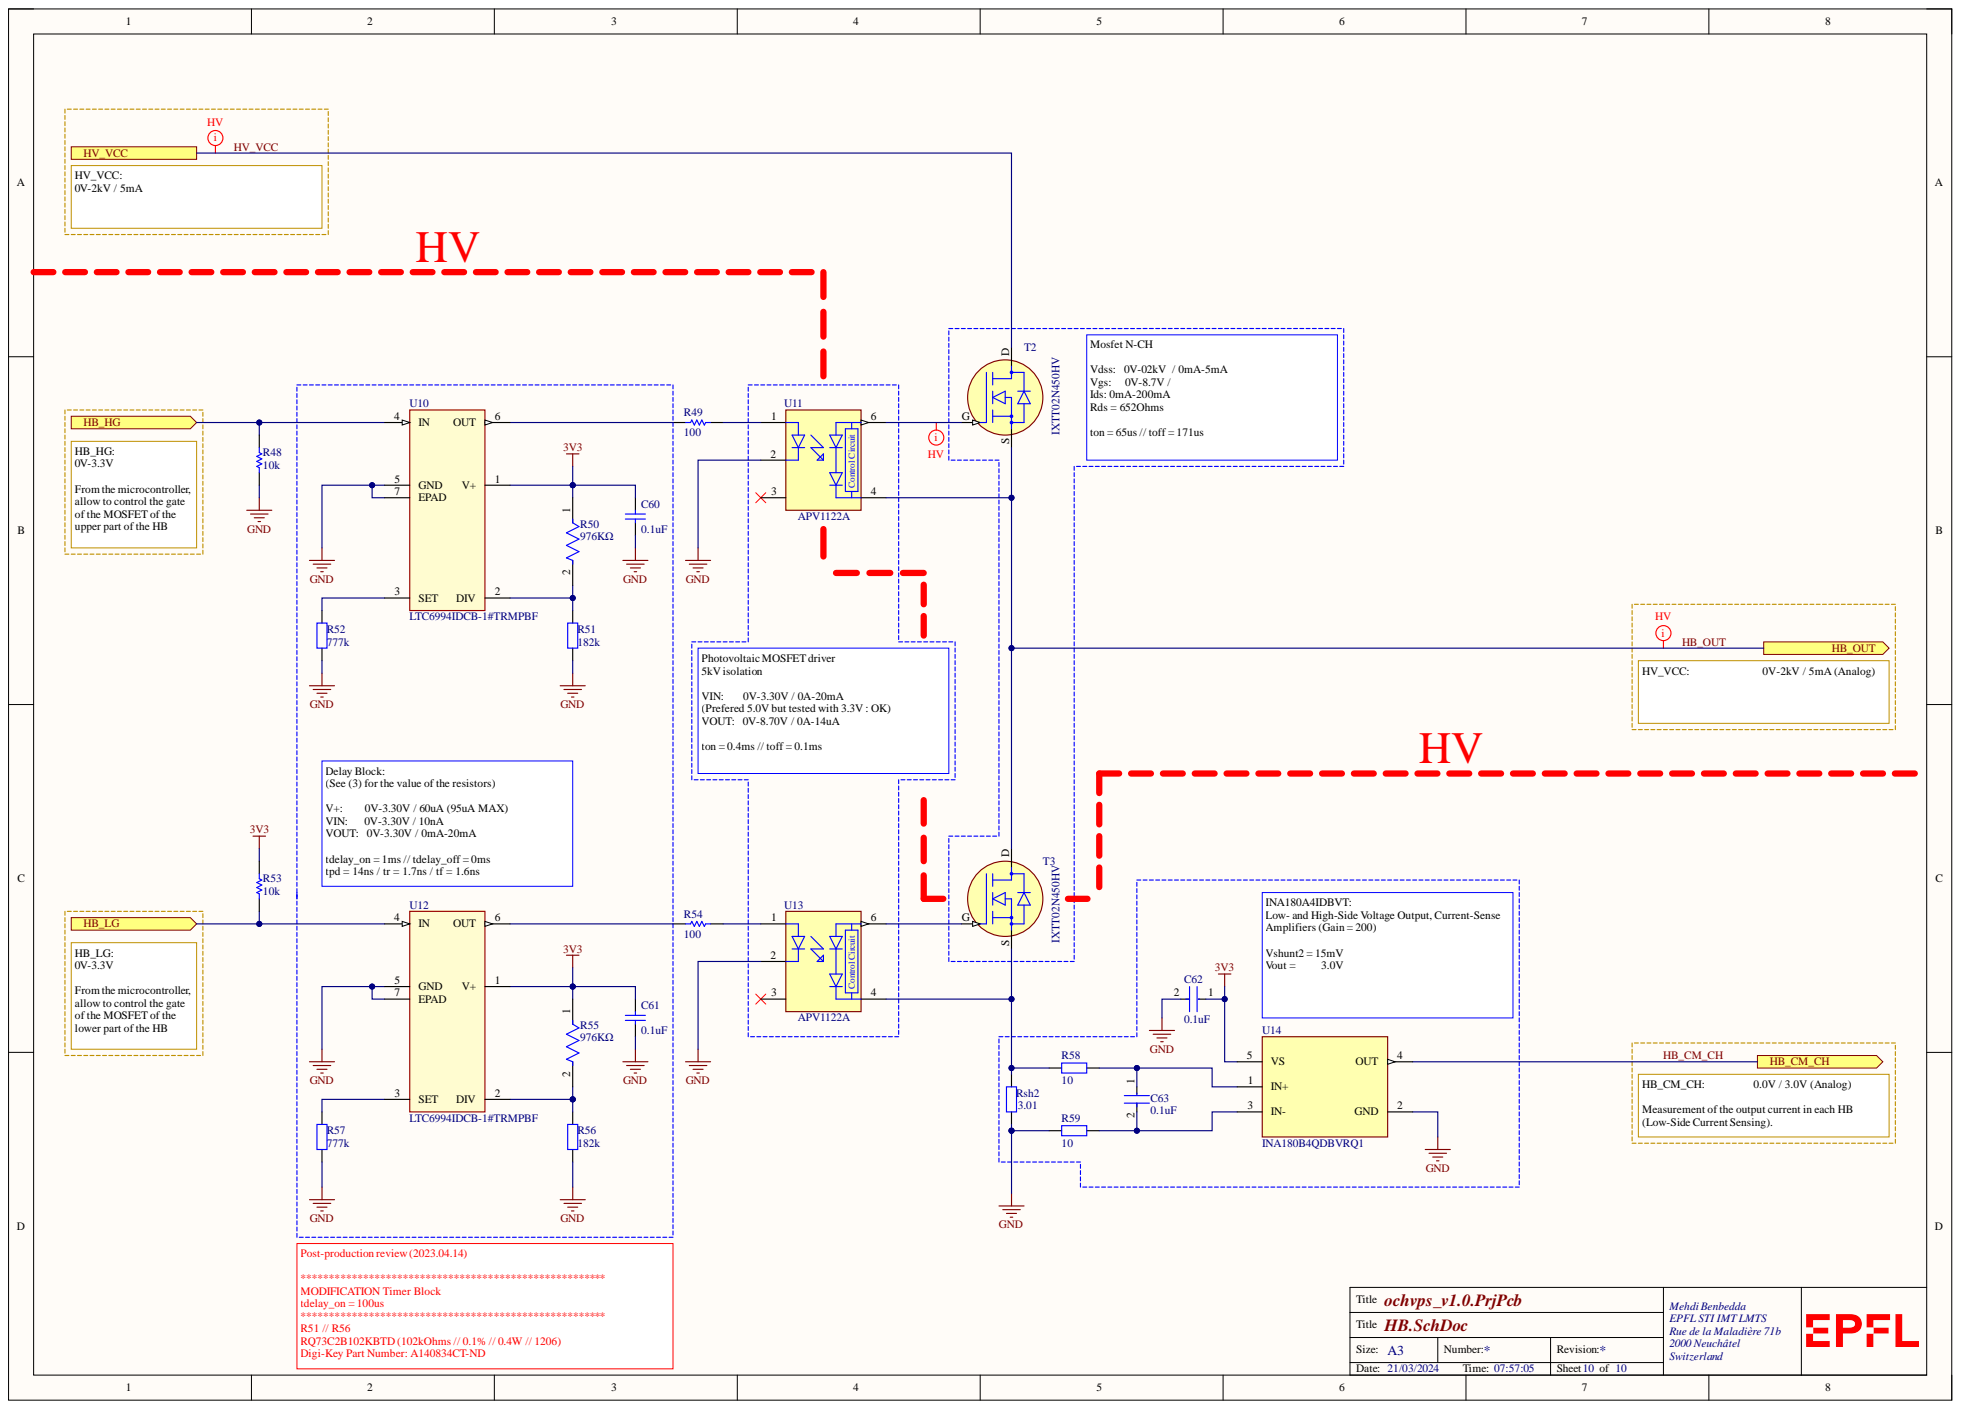
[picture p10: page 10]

HV_VCC | HV

HV_VCC: 0V-2kV / 5mA

From the microcontroller,
allow to control the gate
of the MOSFET of the
upper part of the HB

(Prefered 5.0V but tested with 3.3V : OK)
VOUT: 0V-8.70V / 0A-14uA

Delay Block:
(See (3) for the value of the resistors)

INA180A4IDBVT:
Low- and High-Side Voltage Output, Current-Sense
Amplifiers (Gain = 200)

lower part of the HB

Measurement of the output current in each HB
(Low-Side Current Sensing).
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
